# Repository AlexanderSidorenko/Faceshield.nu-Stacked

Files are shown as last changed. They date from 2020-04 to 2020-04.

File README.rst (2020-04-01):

Overview
========
This repo contains a short `OpenSCAD <https://www.openscad.org/>`_ script that generates a stack of 3D printable face shields designed by 3D Verkstan. You can find more information about the original design on `their official web site <https://3dverkstan.se/protective-visor/>`_. Original STL files can be found in their `GitHub repo <https://github.com/Cederb/Faceshield.nu/>`_.

Solid forehead version
======================
Originally I tried stacking `V3, 6 hole, US version STL <https://github.com/Cederb/Faceshield.nu/blob/master/North%20America/3D%20Printing%20Files%20(STL)/Visor_Frame_NORTH_AMERICA_letter_6-hole_v3.stl>`_ from 3D Verkstan, but after printing a couple of small, test stacks, I discovered the original design doesn't stack well.

The problem happens due to the hollowing in the forehead area. When printing original (hollowed) version of the part with thick layers (I am printing ``0.4mm`` think layers), there are only few layers in the forehead area (in case of ``0.4mm`` layers, only 2). The first layer "hangs" over the hollow area in the part below, and doesn't adhere to the second layer. This results in very brittle parts. The hollowing was probably added to reduce print time and save material, but unfortunately it makes it harder to stack the parts.

I remixed the part to fill the hollowing in the forehead area. You can find it under name ``Visor_Frame_NORTH_AMERICA_letter_6-hole_v3_solid_forehead.stl``.

In my experience, filling the hollowing doesn't significantly impact the print time and/or material usage.

When sliced using ``0.6mm`` nozzle, ``0.4mm`` layer height and ``30%`` rectilinear infill for ``Original Prusa i3 MK3``, ``PrusaSlicer`` produces the following estimates. The original (hollowed) model uses ``15.94g`` of PETG and takes ``34`` minutes to print. The remixed (solid) model uses ``18.91g`` of PETG and takes ``39`` minutes to print. The difference isn't that big, but allows for better stacking.

I left an option to stack hollowed version of the part. I had bad luck with that, but YMMV.

General comments
================
The script stacks the STLs up to specified number, leaving a specified gap in between.

Optionally, it can also insert a flat "spacer" between the parts to make separation easier. I tried to address the issue with the hollowing using a spacer. I had no luck with this approach, but, again, YMMV.

Last, but not least, there are 1 (or 3 if stacking hollowed) cylindrical pillars added that are going through all the parts. They are necessary for 2 reasons:

1. Without the pillars, some slicers complain that there are empty layers and refuse to slice. Since we left the empty layers by design, this is a great hack to trick the slicer.
2. When printing hollowed, pillars help support layers that are hanging in the air.

Parameters
==========

``N`` - number of parts in the stack.

``gap`` - total gap, in millimeters, to be left between two parts. Has to be at least ``spacer_thickness``.

``pillar_radius`` - radius of cylindrical pillars.

``spacer_thickness`` - thickness, in millimeters, of the spacer. Can be 0. Please note that thickness of the spacer is not added to ``gap``! In other words, the total gap is shared by the spacer and the actual gap. I had no luck with spacers, but YMMV, so I left the option in.

``solid_forehead`` - if 0, this will use the original (hollowed) version of the part model, and add 3 pillars. I had no luck with this approach, but YMMV.

My experience printing
======================
I successfully printed a couple of stacks, all ``30`` high, on an ``Original Prusa i3 MK3``. I used ``0.6mm`` nozzle, ``0.4mm`` layer height, ``30%`` rectilinear infill and ``AmazonBasics PETG filament``.

The gap of ``0.4mm`` and no spacer worked great for me! YMMV, and **different combinations of nozzle diameter/layer thickness will most likely require different parameters!**

You can find the STL that worked for me in this repo.

Coming soon: "the splitter"
===========================
Once stack is printed, parts need to be split apart. I am in the process of designing a 3D printable "splitter" that will make it easier.

The first iteration of the design almost worked, but needs some further tweaks. I will update the repo when I have the design fine-tuned and verified to work.

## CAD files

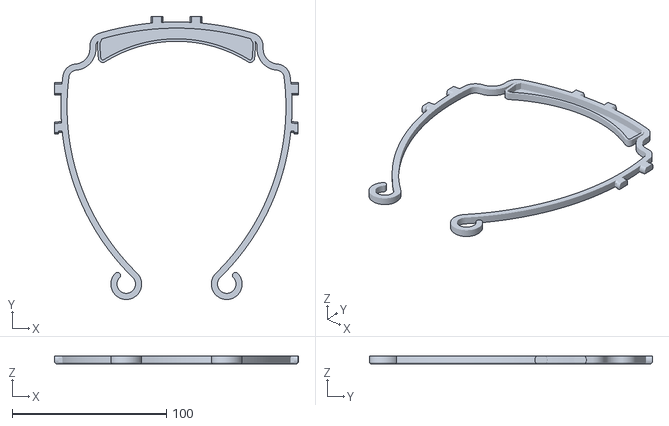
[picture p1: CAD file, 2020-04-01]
Visor_Frame_NORTH_AMERICA_letter_6-hole_v3.stl
158.5 x 183.6 x 5.00

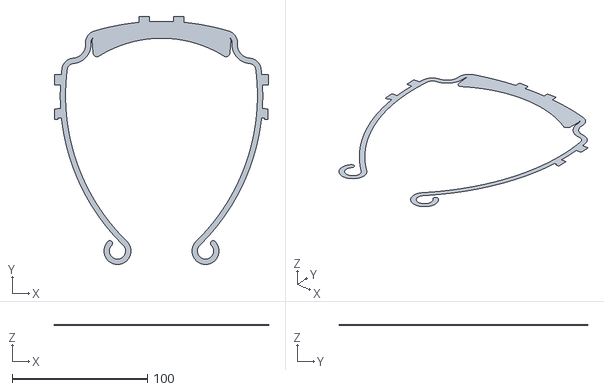
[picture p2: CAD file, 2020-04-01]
Visor_Frame_NORTH_AMERICA_letter_6-hole_v3_spacer_0.2.stl
158.5 x 183.6 x 0.2

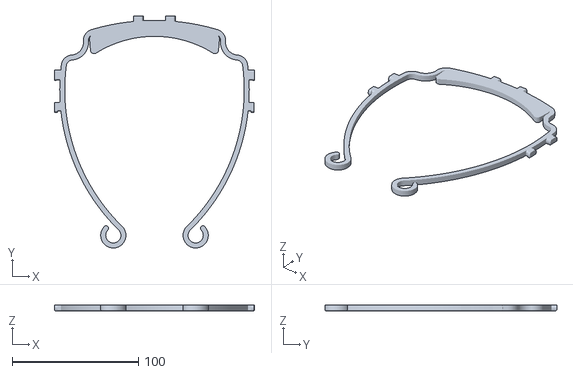
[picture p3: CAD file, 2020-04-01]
Visor_Frame_NORTH_AMERICA_letter_6-hole_v3_solid_forehead.stl
158.5 x 183.6 x 5.00

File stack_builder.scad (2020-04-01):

N = 30;
gap = 0.4;

// Constant - usually don't need to change.
pillar_radius = 1.5;
// Constant - usually don't need to change.
spacer_thickness = 0.0;
// Constant - usually don't need to change.
part_height = 5; // height, in mm, of the part.
// Constant - usually don't need to change.
pillar_facets = 32; // number of facets on cylindrical pillars.
// Constant - usually don't need to change.
solid_forehead = 1;

module part()
{
    if (solid_forehead)
    {
        import("Visor_Frame_NORTH_AMERICA_letter_6-hole_v3_solid_forehead.stl");
    }
    else
    {
        import("Visor_Frame_NORTH_AMERICA_letter_6-hole_v3.stl");
    }
}

module spacer(spacer_thickness)
{
    translate([0, 0, -spacer_thickness / 2]) scale ([1, 1, spacer_thickness / 0.2]) import("Visor_Frame_NORTH_AMERICA_letter_6-hole_v3_spacer_0.2.stl");
}

module part_and_spacer(gap, spacer_thickness, spacer_needed)
{
    part();
    if (spacer_needed)
    {
        translate([0, 0, part_height+gap / 2]) spacer(spacer_thickness);
    }
}

module pillar(parts_distance)
{
    // OpenSCAD is super picky about surfaces of objects being united not being in the same plane.
    // So we have to make ends of the pillars penetrate into the parts both at the top and at the bottom.
    margin = 0.2;
    pillar_height = (N - 1) * parts_distance;
    translate([0, 0, margin]) cylinder(h = pillar_height, r1 = pillar_radius, r2 = pillar_radius, $fn=pillar_facets);
}

module stack(N, gap, spacer_thickness, pillar_radius)
{
    union()
    {
        parts_distance = gap + part_height;
        for (i = [0:N-1])
        {
            translate([0, 0, i * parts_distance]) part_and_spacer(gap, spacer_thickness, i < N-1);
        }
        if (!solid_forehead)
        {
            for (i = [-1:2:1])
            {
                translate([i * 40, 15, 0]) pillar(parts_distance);
            }
        }
        translate([0, 22, 0]) pillar(parts_distance);
    }
}
stack(N, gap, spacer_thickness, pillar_radius);
